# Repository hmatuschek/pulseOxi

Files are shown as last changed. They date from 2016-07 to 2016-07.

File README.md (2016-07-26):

# A USB pulse oximeter 

An pulse oximeter is a relatively simple device. It uses the property of hemoglobin to change its absorption spectrum around 660nm (red) and to some lesser degree around 940nm (infrared) when saturated with oxygen. This change in the absorption spectrum can therefore be measured indirectly by measuring the amount (intensity, brightness) of red and infrared light being transmitted through or back-scattered from e.g. a finger. 

The absolute amount of light that gets detected, however, depends on many factors, including the sensitivity of the detector (photo diode), the light source (LEDs), how the detector and sources are fixated on the skin and, of course, on physiognomic properties of the finger. These dependencies turn the measurement with a single light source virtually impossible. Many of these influences, however, affect light of all wavelengths. Hence it is possible to reduce these influences on the measurement by measuring the brightness of light of more than one wavelength. The oxidation of hemoglobin changes its absorption at different wavelengths differently, hence using two light sources with different wavelengths allows to cancel out the influences which are wavelength insensitive. This "trick" then allows to measure the oxidation of the hemoglobin by measuring the change in the difference of the intensities at these two wavelengths. 

## The hardware

For the [circuit](https://github.com/hmatuschek/pulseOxi/blob/master/hardware/pulse_scm.pdf), two LEDs are used as light sources. One red led (around 645nm) and one infra red (IR, 900nm) led. The intensity of the transmitted light is then measured using a photo diode. The current through this diode is then converted to a voltage using a operational amplifier (opamp). The voltage signal is then sampled using one of the analog/digital converters (ADCs) of the ATtiny45. By switching the LEDs on and off (also controlled by the ATtiny), the intensity difference can be computed, representing the relative oxidation level of the hemoglobin. For more details on how to construct a pulse-oximeter, consider the [AN4327 application node](http://www.nxp.com/files/32bit/doc/app_note/AN4327.pdf) by NXP. 

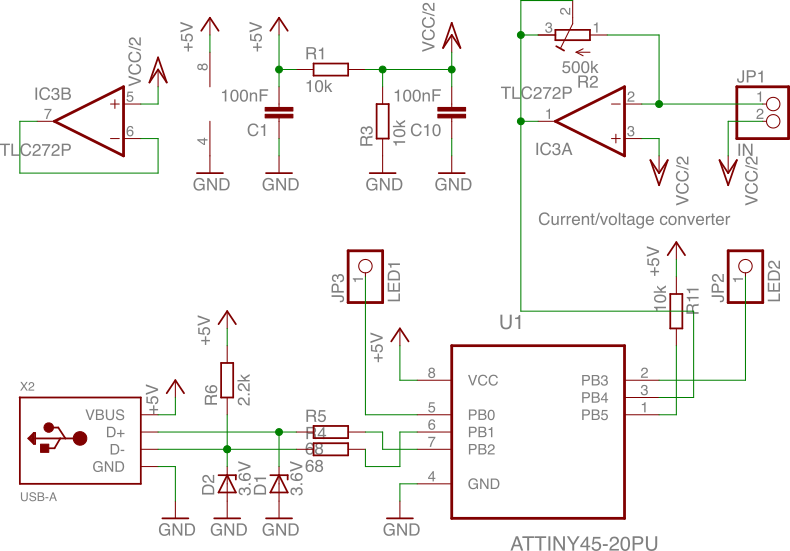
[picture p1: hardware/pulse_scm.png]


This circuit is very reduced. It was designed as a USB dongle without using SMD parts. Hence many parts usually enhancing the circuit stability and reliability have been omitted and should be added when a larger form factor is chosen. For example, I omitted:

  * LED driver circuits,
  * A proper blocking pi-network or even a larger blocking capacitor to stabilize the supply voltage, 
  * A small capacitor in parallel to the feed-back resistor of the transimpedance amplifier,
  * A proper reference voltage for the transimpedance amplifier.

Given the simplicity of the circuit, the results are surprisingly good. 

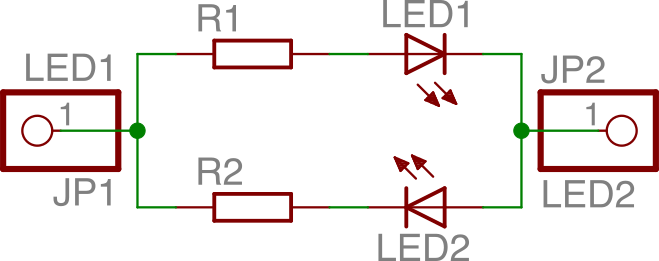
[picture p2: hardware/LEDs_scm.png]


Please note that the LEDs are driven directly by the digital outputs of the ATtiny. They are able to deliver (only) about 20-30mA. Hence choose the LEDs and their series resistors accordingly. The circuit above does not include the series resistors. They are connected directly to the LEDs at the clip. The single LEDs are driven by ATtiny in a H-bridge way. That is, one of the LED pins acts as a source and one as a sink. This allows to drive the LEDs with two wires only but does not allow for driving them both simultaneously. Hence the LEDs must be connected to the ATtiny like shown in the circuit above.

## The client software

The client software provides a convenient [Qt5](https://qt.io) GUI application using [QCustomPlot](http://www.qcustomplot.com/) for potting and [libusb](http://libusb.info/) to interface the pulse oximeter hardware.

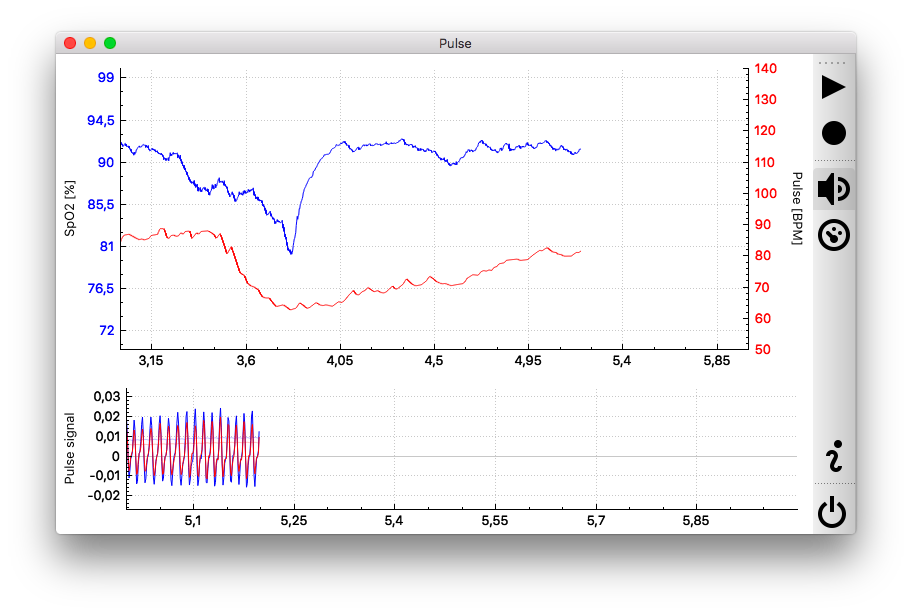
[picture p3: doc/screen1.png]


The upper half shows the (approx.) SpO2 level (relative oxygen saturation, blue line) together with an estimate of the pulse rate in BPM (red line). The smaller bottom plot shows the pulse signal obtained for the IR channel (blue line) and red channel (red line) from which the pulse rate gets estimated. With the current implementation, the baseline and AC signal (deviance from the baseline) as well as the amplitude of the AC signal are obtained using sinc-convolution filters. This implies a short delay (about 5s) between the actual measurement and the display.

## Features

 * Small circuit.
 * USB interface using [V-USB](https://www.obdev.at/products/vusb/index-de.html).
 * USB powered.

## License
Pulse - A simple pulse oximeter. (c) 2015 Hannes Matuschek <hmatuschek at gmail dot com>

The hardware is licensed under [Createtive Commons BY-SA 4.0](https://creativecommons.org/licenses/by-sa/4.0/) and the software under [GPL 2.0+](https://www.gnu.org/licenses/old-licenses/gpl-2.0.txt) (see below).

This program is free software; you can redistribute it and/or
modify it under the terms of the GNU General Public License
as published by the Free Software Foundation; either version 2
of the License, or (at your option) any later version.</p>

This program is distributed in the hope that it will be useful,
but WITHOUT ANY WARRANTY; without even the implied warranty of
MERCHANTABILITY or FITNESS FOR A PARTICULAR PURPOSE.  See the
GNU General Public License for more details.

You should have received a copy of the GNU General Public License
along with this program; if not, write to the Free Software
Foundation, Inc., 51 Franklin Street, Fifth Floor, Boston, MA  02110-1301, USA.

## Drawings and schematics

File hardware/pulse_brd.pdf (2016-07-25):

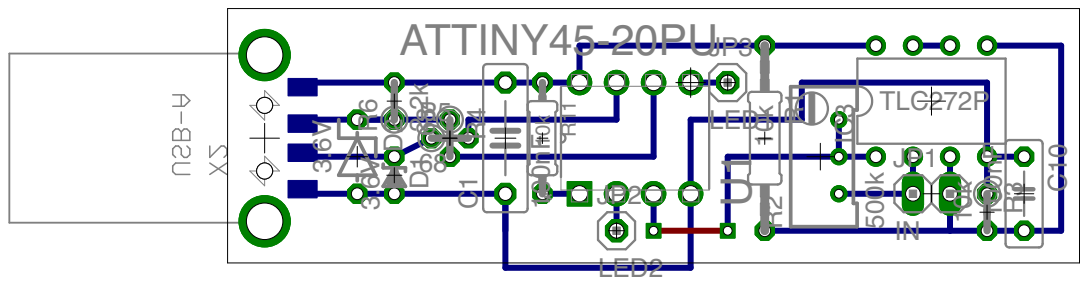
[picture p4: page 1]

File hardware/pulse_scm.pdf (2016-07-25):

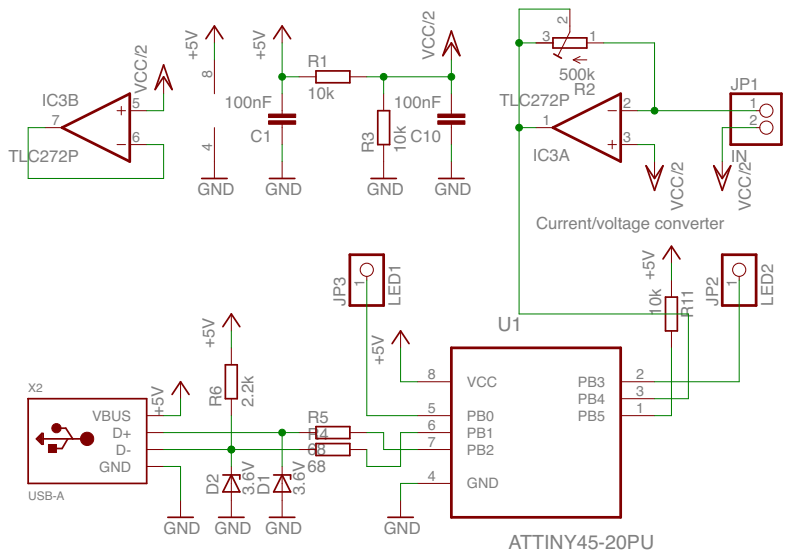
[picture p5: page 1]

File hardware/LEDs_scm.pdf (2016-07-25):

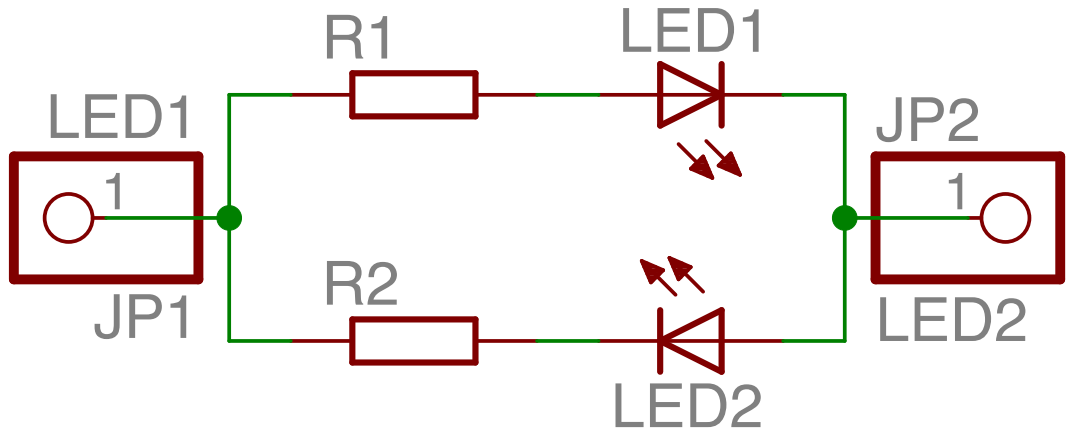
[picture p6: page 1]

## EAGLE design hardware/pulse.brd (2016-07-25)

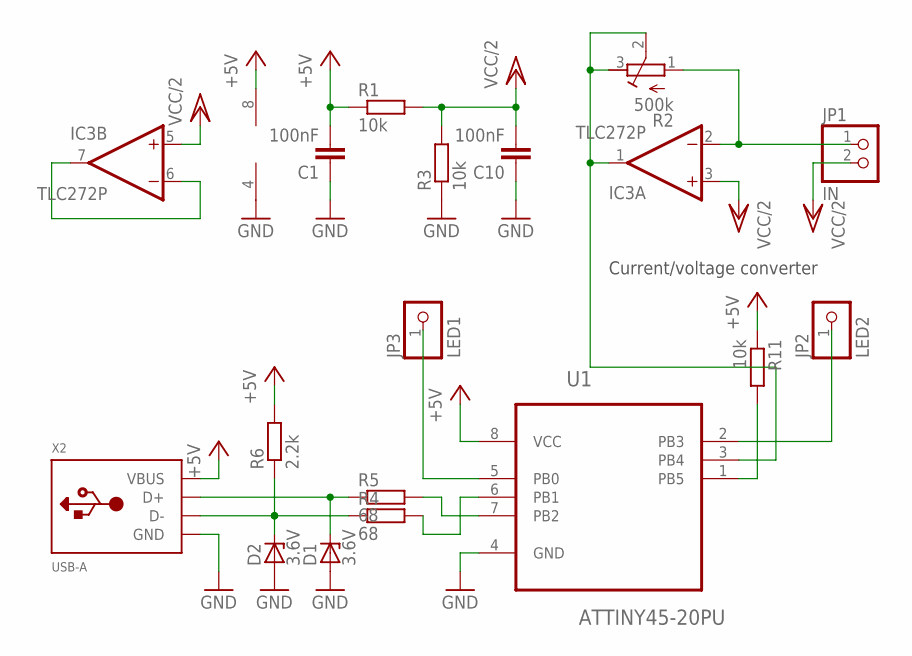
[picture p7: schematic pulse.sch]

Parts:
C1: 100nF; C075-032X103
C10: 100nF; C050-025X075
D1: 3.6V; ZDIO-2.5
D2: 3.6V; ZDIO-5
IC3: TLC272P; DIL08
JP1: IN; 1X02
JP2: LED2; 1X01
JP3: LED1; 1X01
R1: 10k; 0207/12
R2: 500k; RTRIM64W
R3: 10k; 0204V
R4, R5: 68; 0204V
R6: 2.2k; 0204V
R11: 10k; 0204/7
U1: ATTINY45-20PU; DIP254P762X533-8
X2: USB-A; MOLEX_480371000

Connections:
+5V: C1.2, IC3.8 (V+), R1.1, R6.2, R11.1, U1.8 (VCC), X2.1 (VBUS)
GND: C1.1, C10.1, D1.A, D2.A, IC3.4 (V-), R3.1, U1.4 (GND), X2.4 (GND)
unnamed: IC3.2 (-IN), JP1.1, R2.1 (A)
unnamed: R5.2, U1.7 (PB2)
unnamed: R4.2, U1.6 (PB1)
unnamed: JP2.1, U1.2 (PB3)
unnamed: JP3.1, U1.5 (PB0)
unnamed: IC3.6 (-IN), IC3.7 (OUT)
unnamed: IC3.1 (OUT), R2.2 (S), R2.3 (E), U1.3 (PB4)
unnamed: R11.2, U1.1 (PB5)
unnamed: D1.C, R5.1, X2.3 (D+)
unnamed: D2.C, R4.1, R6.1, X2.2 (D-)
VCC/2: C10.2, IC3.3 (+IN), IC3.5 (+IN), JP1.2, R1.2, R3.2

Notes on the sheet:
Current/voltage converter

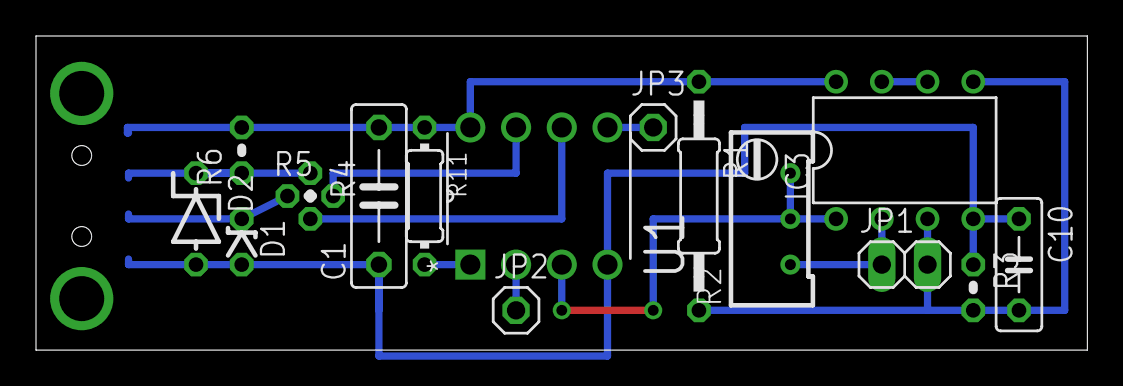
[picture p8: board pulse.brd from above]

Board: 2 copper layers, 58.4 x 17.5 mm, 17 parts (1 on the bottom side), 13 nets.

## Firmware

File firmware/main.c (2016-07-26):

#include <avr/io.h>
#include <avr/interrupt.h>
#include <util/delay.h>
#include <avr/pgmspace.h>
#include <avr/eeprom.h>
#include "usbdrv/usbdrv.h"
#include "proto.h"


#define PULSE_LED1_PORT    B
#define PULSE_LED1_PIN     0

#define PULSE_LED2_PORT    B
#define PULSE_LED2_PIN     3

#define PULSE_ADC_PORT     B
#define PULSE_ADC_PIN      4
#define PULSE_ADC_CHANNEL  2


#define PULSE_CONCAT(a,b)   a ## b
#define DDR_REG_NAME(port)  PULSE_CONCAT(DDR, port)
#define PORT_REG_NAME(port)  PULSE_CONCAT(PORT, port)

#define LED1_DDR_REG        DDR_REG_NAME(PULSE_LED1_PORT)
#define LED1_PORT_REG       PORT_REG_NAME(PULSE_LED1_PORT)

#define LED2_DDR_REG        DDR_REG_NAME(PULSE_LED2_PORT)
#define LED2_PORT_REG       PORT_REG_NAME(PULSE_LED2_PORT)

#define ADC_DDR_REG         DDR_REG_NAME(PULSE_ADC_PORT)
#define ADC_PORT_REG        PORT_REG_NAME(PULSE_ADC_PORT)
#define ADC_MUX             (PULSE_ADC_CHANNEL & 0x0f)

#define NOP                 asm volatile ("nop")

// ==============================================================================
// Globals
// ------------------------------------------------------------------------------

static Message usb_reply;
static uint16_t currentSum = 0;
static uint8_t  sampleCount = 0;

typedef enum {
  MODE_IDLE,
  MODE_START,
  MODE_LED1,
  MODE_LED2,
  MODE_BASE,
  MODE_READY
} Mode;

static Mode mode = MODE_IDLE;


// ------------------------------------------------------------------------------
// - usbFunctionSetup
// - see: http://vusb.wikidot.com/driver-api
// ------------------------------------------------------------------------------
usbMsgLen_t usbFunctionSetup(uchar data[8]) {
  usbRequest_t    *rq = (void *)data;
  // Dispatch by request type
  if ((MODE_READY == mode) && (rq->bRequest == PULSE_CMD_GET)) {
    // If there is some data and CMB is GET
    usbMsgLen_t len = sizeof(usb_reply);
    if (len > rq->wLength.word)
      len = rq->wLength.word;
    usbMsgPtr = (void *) &usb_reply;
    mode = MODE_IDLE;
    return len;
  } else if ((MODE_IDLE == mode) && (rq->bRequest == PULSE_CMD_START)) {
    // If idle and CMD is START
    mode = MODE_START;
  }
  return 0;
}


/* ********************************************************************************************* *
 * Hardware setup
 * ********************************************************************************************* */
static void
hardwareInit(void) {
  // Init USB interface
  uchar i, j;

  /* deactivate pull-ups on USB lines */
  USB_CFG_IOPORT &= ~ ((1 << USB_CFG_DMINUS_BIT) | (1 << USB_CFG_DPLUS_BIT));
  USBDDR |= (1 << USB_CFG_DMINUS_BIT) | (1 << USB_CFG_DPLUS_BIT);

  j = 0;
  while (--j) {		/* USB Reset by device only required on Watchdog Reset */
    i = 0;
    while (--i);	/* delay >10ms for USB reset */
  }

  /*  remove USB reset condition */
  USBDDR &= ~ ( (1 << USB_CFG_DMINUS_BIT) | (1 << USB_CFG_DPLUS_BIT) );

  // Set LED output
  LED1_DDR_REG |= (1<<PULSE_LED1_PIN);
  LED2_DDR_REG |= (1<<PULSE_LED2_PIN);
  // Shut LEDs off
  LED1_PORT_REG &= ~(1<<PULSE_LED1_PIN);
  LED2_PORT_REG &= ~(1<<PULSE_LED2_PIN);
  // Set ADC pin input & disable pull-up
  ADC_DDR_REG &= ~(1<<PULSE_ADC_PIN);
  ADC_PORT_REG &= ~(1<<PULSE_ADC_PIN);

  // Config ADC (2.56V ref, right adjust, selected pin)
  ADMUX |= (1<<REFS2) | (1<<REFS1) | (0<<REFS0) | (0<<ADLAR) | ADC_MUX;
  // config prescaler to 128
  ADCSRA |= (1<<ADPS2) | (1<<ADPS1) | (1<<ADPS0);
  // enable ADC
  ADCSRA |= (1<<ADEN);

  // init state machine in "idle"
  mode = MODE_IDLE;
}


/* ********************************************************************************************* *
 * Measurement loop
 * ********************************************************************************************* */
static void
adcPoll() {
  // Dispatch by mode
  if (MODE_START == mode) {
    // enable LED1 & disable LED2
    LED1_PORT_REG |= (1<<PULSE_LED1_PIN);
    LED2_PORT_REG &= ~(1<<PULSE_LED2_PIN);
    NOP;
    // start converion
    ADCSRA |= (1<<ADSC);
    // update mode
    mode = MODE_LED1;
    // reset counter
    currentSum = 0;
    sampleCount = 0;
  } else if ((MODE_LED1 == mode) && (0 == (ADCSRA & (1<<ADSC)))) {
    // add result to sum
    currentSum += ADC;
    sampleCount++;
    if (64 > sampleCount) {
      // start converion
      ADCSRA |= (1<<ADSC);
    } else {
      // store 16 bit value
      usb_reply.lower = currentSum;
      // reset counter
      currentSum = 0; sampleCount = 0;
      // disable LED1 & enable LED2
      LED1_PORT_REG &= ~(1<<PULSE_LED1_PIN);
      LED2_PORT_REG |= (1<<PULSE_LED2_PIN);
      NOP;
      // start converion
      ADCSRA |= (1<<ADSC);
      // update mode
      mode = MODE_LED2;
    }
  } else if ((MODE_LED2 == mode) && (0 == (ADCSRA & (1<<ADSC)))) {
    // add result to sum
    currentSum += ADC;
    sampleCount++;
    if (64 > sampleCount) {
      // start converion
      ADCSRA |= (1<<ADSC);
    } else {
      // store 16 bit value
      usb_reply.upper = currentSum;
      // reset counter
      currentSum = 0; sampleCount = 0;
      // disable LED 1 & 2
      LED1_PORT_REG &= ~(1<<PULSE_LED1_PIN);
      LED2_PORT_REG &= ~(1<<PULSE_LED2_PIN);
      NOP;
      // update mode, done.
      mode = MODE_BASE;
      // start converion
      ADCSRA |= (1<<ADSC);
    }
  } else if ((MODE_BASE == mode) && (0 == (ADCSRA & (1<<ADSC)))) {
    // add result to sum
    currentSum += ADC;
    sampleCount++;
    if (64 > sampleCount) {
      // start converion
      ADCSRA |= (1<<ADSC);
    } else {
      // store 16 bit value
      usb_reply.base = currentSum;
      // reset counter
      currentSum = 0; sampleCount = 0;
      // update mode
      mode = MODE_READY;
    }
  }
}


/* ------------------------------------------------------------------------- */
/* ------------------------ Oscillator Calibration ------------------------- */
/* ------------------------------------------------------------------------- */

/* Calibrate the RC oscillator to 8.25 MHz. The core clock of 16.5 MHz is
 * derived from the 66 MHz peripheral clock by dividing. Our timing reference
 * is the Start Of Frame signal (a single SE0 bit) available immediately after
 * a USB RESET. We first do a binary search for the OSCCAL value and then
 * optimize this value with a neighboorhod search.
 * This algorithm may also be used to calibrate the RC oscillator directly to
 * 12 MHz (no PLL involved, can therefore be used on almost ALL AVRs), but this
 * is wide outside the spec for the OSCCAL value and the required precision for
 * the 12 MHz clock! Use the RC oscillator calibrated to 12 MHz for
 * experimental purposes only!
 */
static void
calibrateOscillator(void) {
  uchar       step = 128;
  uchar       trialValue = 0, optimumValue;
  int         x, optimumDev, targetValue = (unsigned)(1499 * (double)F_CPU / 10.5e6 + 0.5);

  /* do a binary search: */
  do{
    OSCCAL = trialValue + step;
    x = usbMeasureFrameLength();    /* proportional to current real frequency */
    if(x < targetValue)             /* frequency still too low */
      trialValue += step;
    step >>= 1;
  }while(step > 0);
  /* We have a precision of +/- 1 for optimum OSCCAL here */
  /* now do a neighborhood search for optimum value */
  optimumValue = trialValue;
  optimumDev = x; /* this is certainly far away from optimum */
  for(OSCCAL = trialValue - 1; OSCCAL <= trialValue + 1; OSCCAL++){
    x = usbMeasureFrameLength() - targetValue;
    if(x < 0)
      x = -x;
    if(x < optimumDev){
      optimumDev = x;
      optimumValue = OSCCAL;
    }
  }
  OSCCAL = optimumValue;
}

void
usbEventResetReady(void) {
  /* Disable interrupts during oscillator calibration since
   * usbMeasureFrameLength() counts CPU cycles. */
  cli();
  calibrateOscillator();
  sei();
  eeprom_write_byte(0, OSCCAL);   /* store the calibrated value in EEPROM */
}


/* ********************************************************************************************* *
 * main()
 * ********************************************************************************************* */
int
main(void)
{
  // Init hardware
  hardwareInit();
  usbInit();

  // Enable interrupts
	sei();

	for(;;) {
    // handle USB stuff
    usbPoll();
    // handle measurement stuff
    adcPoll();
	}

  return 0;
}

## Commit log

2015-11-03 Added first version of the circuit.
    [pulse.sch]
2015-11-04 Fixed circuit and board.
    [pulse.brd, pulse.sch]
2016-07-19 Rewritten to large parts.
    [pulse.brd, pulse.sch]
2016-07-19 Fixed minors.
    [pulse.brd, pulse.sch]
2016-07-25 Added schematic print.
2016-07-25 Added LED circ.
    [LEDs.sch]
2016-07-25 Updated schematic & board.
    [pulse.brd, pulse.sch]
2016-07-26 Updated V-USB driver & added RC calibration.
